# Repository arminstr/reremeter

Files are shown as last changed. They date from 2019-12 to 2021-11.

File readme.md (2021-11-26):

# reremeter

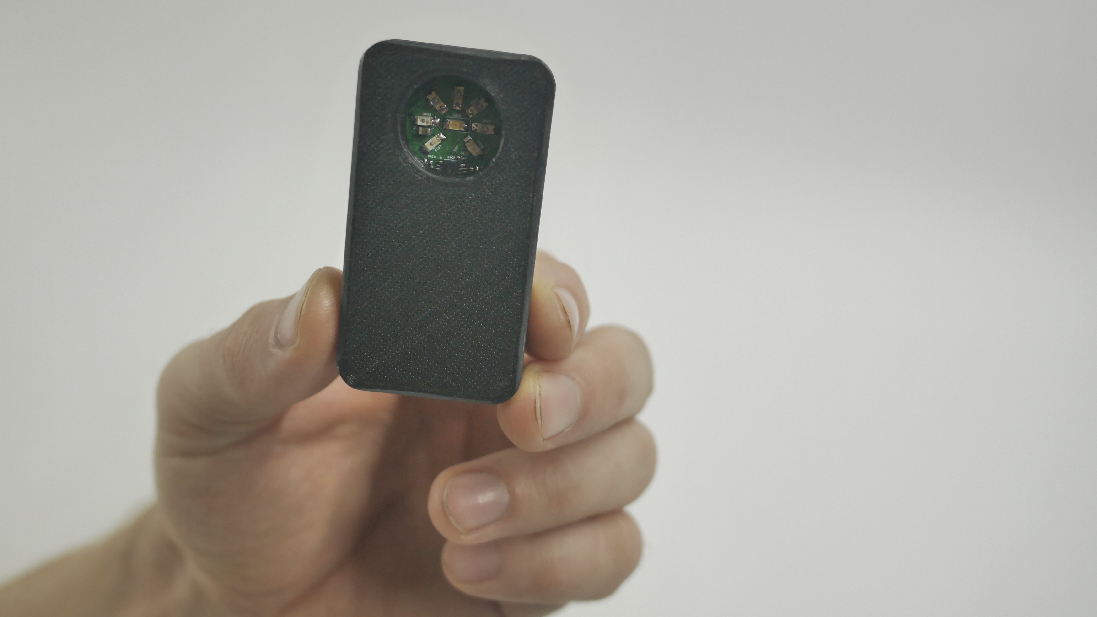
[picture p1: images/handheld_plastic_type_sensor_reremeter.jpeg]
Picture of reremeter


Reremeter is an handheld and low-cost discrete near infrared reflectance spectrometer and a machine learning algorithm developed to detect different types of plastic. Watch our [video](https://www.youtube.com/watch?v=hrVgNUm2_Jo) to find out more!

This repository contains all the files required to build an reremeter from scratch, and you can use them to make your own version. Please take note that this work is published under GPL-3.0. 

### How to get started
> Please note the current *Issues* before getting started with the build of your own reremeter.

Now the guide on how to get started with the build of your own reremeter.
- Build your own [hardware](./hardware).
- Build and upload the [firmware](./firmware).
- Collect data of your samples (or check out our example [dataset](./data)).
- Make Predictions using our provided Python [scripts](./software).
- Visualize results in an [UI](./webapp).

### Additional information 
- The main idea behind this project came from reading this paper about [Identification and classification of plastic resins using near infrared reflectance spectroscopy](https://www.researchgate.net/publication/285330830_Identification_and_classification_of_plastic_resins_using_near_infrared_reflectance_spectroscopy) by Hamed Masoumi, Seyed Mohsen Safavi, and Zahra Khani.
- Inspiration for the analog frontend design was given by the [ADS1255](https://www.ti.com/product/ADS1255) reference designs on the TI website. They used this ADC in several DLP NIR spectrometer designs. (e.g. [DLP® NIRscan™ Evaluation Module](https://www.ti.com/tool/DLPNIRSCANEVM#2), [DLP Ultra-mobile NIR Spectrometer for Portable Chemical Analysis with Bluetooth Connectivity](https://www.ti.com/tool/TIDA-00554))
- Super interesting [MEMS spectrum sensor](https://www.hamamatsu.com/eu/en/product/type/C13272-02/index.html). You can read more about this on [OpenRecycling](https://openrecycling.com/en/projects/2021/01/06/plastic-type-sensor.html). 

### Notes
The reremeter project was created at RealRecycling by Armin Straller and Bernhard Gessler.

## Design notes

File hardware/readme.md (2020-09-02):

# reremeter hardware

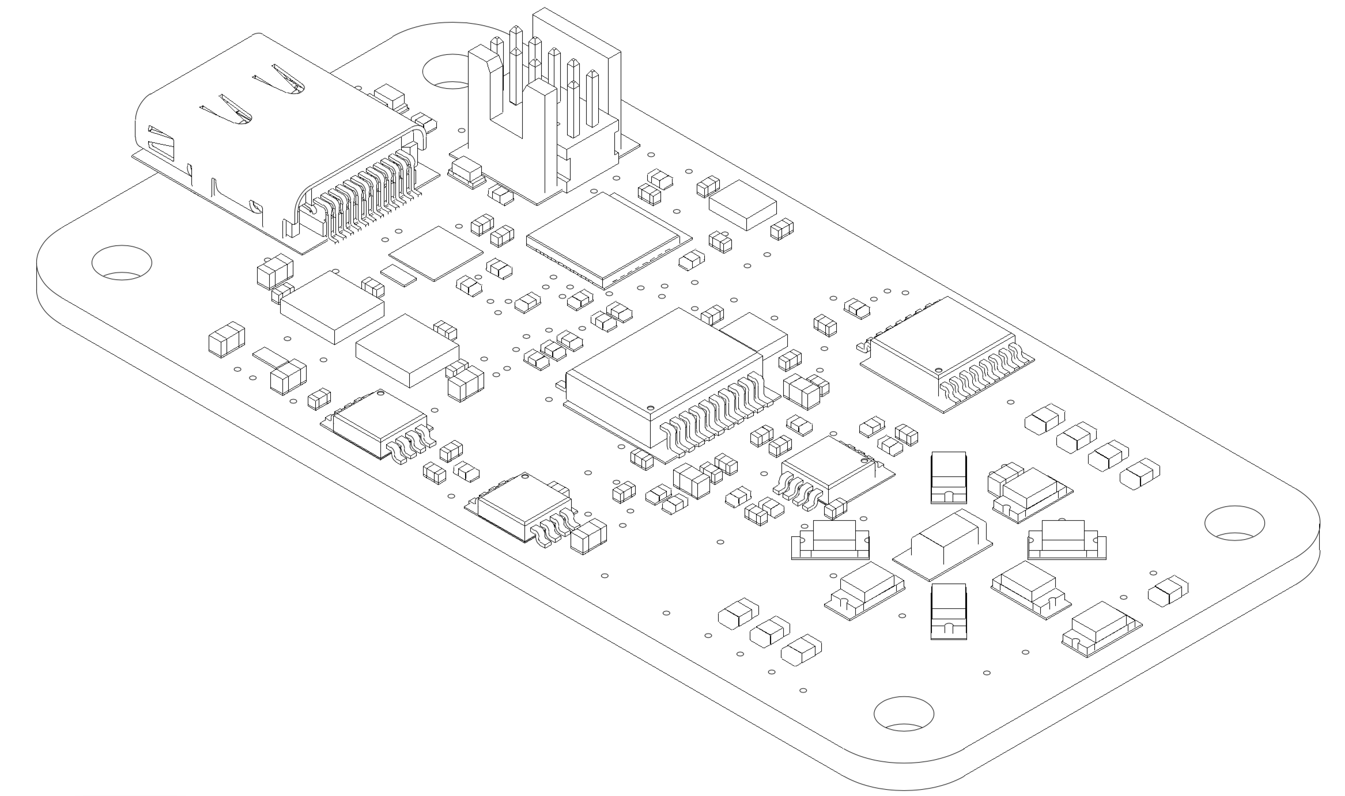
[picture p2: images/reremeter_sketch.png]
Sketch of reremeter exported from CAD model


This folder contains all of the source files for making your own reremeter PCB hardware: a Autodesk Eagle project file for the PCB in spectrometer/, rendered gerber files from the Eagle project in manufacturing/, and exported schematics in this [file](Spectrometer_Schematic.pdf).

The PCB design includes mainly SMT components as the handheld form factor was design criteria. It is possible to assemble individual boards by hand in a few hours (if you bring in decent SMT soldering skills), however for multiple boards it would be advisable to order multiple fully assembled (or at least SMT assembled) PCBs. If you wish to have the PCB manufactured, the files in manufacturing/ should be all you need; additionally, a bill of materials is available [here](manufacturing/Spectrometer_BOM.txt).

Following parts on the BOM previously raised issues:
- X301 is a quartz crystal with 8MHz: FL0800008QDICT-ND
- X302 is a 9pin ARM debug connector: SAM9438-ND
- D20 is a 800nm ~ 1700nm photodetector: 209-003-151-001CT-ND

The mentioned part numbers are from DigiKey. The 8MHz quartz is a replacement part that should fit properly.

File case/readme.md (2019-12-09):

# 3D Printed Case

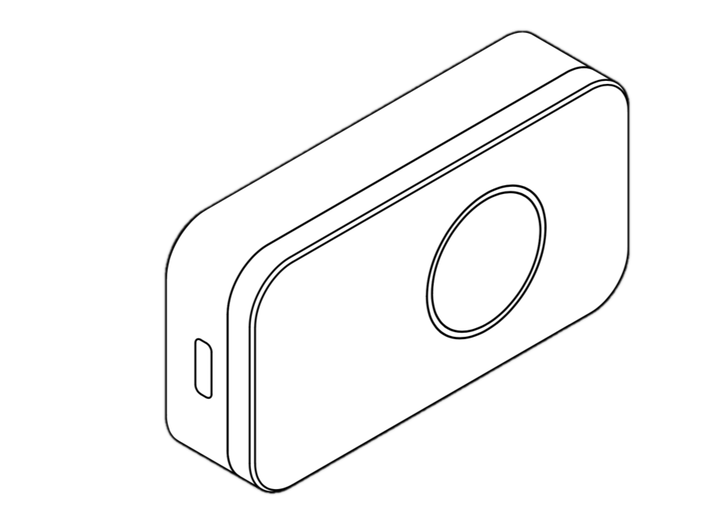
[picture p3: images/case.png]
Picture of case


This directory contains the files we used to 3D print the case for our spectrometer. We highly recommend you printing the same case. It will ensure constant distances to the brightness sensor as well as good handling and protection of the reremeter itself.

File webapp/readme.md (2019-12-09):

# reremeter web interface

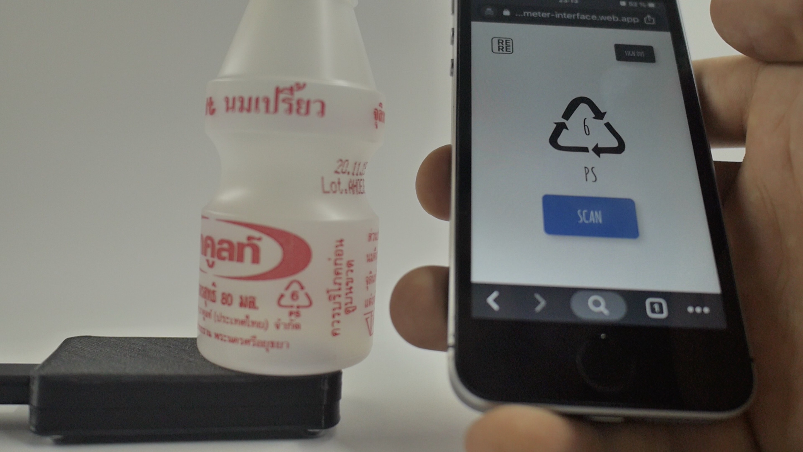
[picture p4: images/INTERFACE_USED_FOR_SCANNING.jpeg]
Picture of web interface


This directory contains the code we used for the scanning interface visible in the above picture. It is a simple HTML, JS and CSS webapp. Using Firebase Authentication and Firebase Realtime Database it is able to run independent of the spectrometers connection. We recommend hosting it with Firebase Hosting for testing.

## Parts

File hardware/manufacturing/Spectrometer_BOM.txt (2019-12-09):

Partlist exported from /Users/armin/CloudStation/02_projects/18_realrecycling/02_dev/01_sensor/02_hardware/pcb/spectrometer/Spectrometer.sch at 07.12.19 15:55

Qty Value                 Device                      Package                 Parts                                                      Description                                 MF MPN               OC_FARNELL OC_NEWARK SPICEPREFIX VALUE    WE-NUMBER               
4   100                   R-EU_R0402                  R0402                   R212, R213, R214, R215                                     RESISTOR, European symbol                                                             R                                            
6   100k                  R-EU_R0402                  R0402                   R108, R208, R209, R210, R211, R308                         RESISTOR, European symbol                                                             R                                            
10  100nF                 C-EUC0402K                  C0402K                  C112, C204, C212, C214, C219, C221, C222, C303, C304, C305 CAPACITOR, European symbol                                                            C                                            
2   100pF                 C-EUC0402K                  C0402K                  C203, C216                                                 CAPACITOR, European symbol                                                            C                                            
2   10k                   R-EU_R0402                  R0402                   R203, R301                                                 RESISTOR, European symbol                                                             R                                            
2   10nF                  C-EUC0402K                  C0402K                  C501, C503                                                 CAPACITOR, European symbol                                                            C                                            
2   10pF                  C-EUC0402K                  C0402K                  C301, C302                                                 CAPACITOR, European symbol                                                            C                                            
2   10uF                  C-EUC0603K                  C0603K                  C504, C513                                                 CAPACITOR, European symbol                                                            C                                            
1   10uF                  C-EUC0805                   C0805                   C201                                                       CAPACITOR, European symbol                                                            C                                            
1   1200nm                LEDCHIPLED_1206             CHIPLED_1206            D105                                                       LED                                                                                                                                
1   1300nm                LEDCHIPLED_1206             CHIPLED_1206            D104                                                       LED                                                                                                                                
1   1450nm                LEDCHIPLED_1206             CHIPLED_1206            D103                                                       LED                                                                                                                                
1   1550nm                LEDCHIPLED_1206             CHIPLED_1206            D102                                                       LED                                                                                                                                
2   15uF                  C-EUC0603K                  C0603K                  C210, C211                                                 CAPACITOR, European symbol                                                            C                                            
1   1650nm                LEDCHIPLED_1206             CHIPLED_1206            D101                                                       LED                                                                                                                                
3   1k                    R-EU_R0402                  R0402                   R302, R303, R304                                           RESISTOR, European symbol                                                             R                                            
1   1k5                   R-EU_R0402                  R0402                   R305                                                       RESISTOR, European symbol                                                             R                                            
6   1uF                   C-EUC0402K                  C0402K                  C207, C208, C209, C307, C502, C507                         CAPACITOR, European symbol                                                            C                                            
2   22R                   R-EU_R0402                  R0402                   R401, R403                                                 RESISTOR, European symbol                                                             R                                            
3   22uF                  C-EUC0805                   C0805                   C105, C205, C206                                           CAPACITOR, European symbol                                                            C                                            
2   240                   WE-CBF_0603_742792631_WB_HS WE-CBF_0603(W=2.2)      FB201, FB401                                               WE-CBF SMD EMI Suppression Ferrite Bead                                                                    742792631/240Ω(Z@100MHz)
2   240k                  R-EU_R0402                  R0402                   R206, R207                                                 RESISTOR, European symbol                                                             R                                            
2   301                   R-EU_R0402                  R0402                   R204, R205                                                 RESISTOR, European symbol                                                             R                                            
1   36                    R-EU_R0603                  R0603                   R107                                                       RESISTOR, European symbol                                                             R                                            
1   39                    R-EU_R0603                  R0603                   R106                                                       RESISTOR, European symbol                                                             R                                            
5   43                    R-EU_R0603                  R0603                   R101, R102, R103, R104, R105                               RESISTOR, European symbol                                                             R                                            
1   47nF                  C-EUC0402K                  C0402K                  C215                                                       CAPACITOR, European symbol                                                            C                                            
2   49.9                  R-EU_R0402                  R0402                   R201, R202                                                 RESISTOR, European symbol                                                             R                                            
2   51pF                  C-EUC0402K                  C0402K                  C217, C218                                                 CAPACITOR, European symbol                                                            C                                            
1   5Vdc/2pF              WE-TVS_SOT23-6L_82400102    WE-TVS_SOT23-6L         D401                                                       WE-TVS TVS Diode – High Speed Series                                                              5Vdc/2pF 82400102                
2   5k1                   R-EU_R0402                  R0402                   R402, R404                                                 RESISTOR, European symbol                                                             R                                            
1   6.8                   R-EU_R0603                  R0603                   R109                                                       RESISTOR, European symbol                                                             R                                            
1   632723300011THT       632723300011THT             USBC_HORZONTAL_WE       X401                                                                                                                                                                                          
1   850nm                 LEDCHIPLED_1206             CHIPLED_1206            D107                                                       LED                                                                                                                                
1   8MHz                  CRYSTALS-GND-LID-CFPX-218   2.6X2.1-4-PAD           X301                                                       CRYSTALS WITH CAN GROUNDED                                                                                                         
1   940nm                 LEDCHIPLED_1206             CHIPLED_1206            D106                                                       LED                                                                                                                                
1   ADS1255TSSOP          ADS1255TSSOP                SOP65P780X200-20        U201                                                                                                                                                                                          
1   CORTEX-MDEBUG-10P     CORTEX-MDEBUG-10P           CORTEX-M-CON-10P        X302                                                                                                                                                                                          
1   LT1763IDE-3.3         LT1763IDE-3.3               DFN12                   IC501                                                      500mA, Low Noise, LDO Micropower Regulators    LT1763IDE-3.3#PBF 1783320    51R1529                                                
1   LT1763IDE-5           LT1763IDE-5                 DFN12                   IC502                                                      500mA, Low Noise, LDO Micropower Regulators    LT1763IDE-5#PBF   1839222    51R1531                                                
4   MOUNT-HOLE2.8         MOUNT-HOLE2.8               2,8                     H1, H2, H3, H4                                             MOUNTING HOLE with drill center marker                                                                                             
1   OPA2376PDSO-8         OPA2376PDSO-8               SOP65P490X110-8         U202                                                                                                                                                                                          
1   OPA350PDSO-8          OPA350PDSO-8                SOP65P490X110-8         U203                                                                                                                                                                                          
1   REF5025PDSO-8         REF5025PDSO-8               SOP65P490X110-8         U204                                                                                                                                                                                          
1   SD003-151-001SMD      SD003-151-001SMD            LEDC3316X110            D201                                                       Surface-Mount InGaAs Photodetector                                                                                                 
1   STM32F302K8U6UFQFPN32 STM32F302K8U6UFQFPN32       QFN50P500X500X60-33T350 U301                                                                                                                                                                                          
1   TLC59208FTSSOP-16     TLC59208FTSSOP-16           SOP65P640X120-16        U101                                                       TLC59208F 8-Bit Fm+ I2C Bus LED Driver                                                                                             
2   green                 LEDCHIP-LED0603             CHIP-LED0603            D301, D303                                                 LED                                                                                                                                
1   orange                LEDCHIP-LED0603             CHIP-LED0603            D302                                                       LED                                                                                                                                
1   white                 LEDCHIPLED_1206             CHIPLED_1206            D108                                                       LED

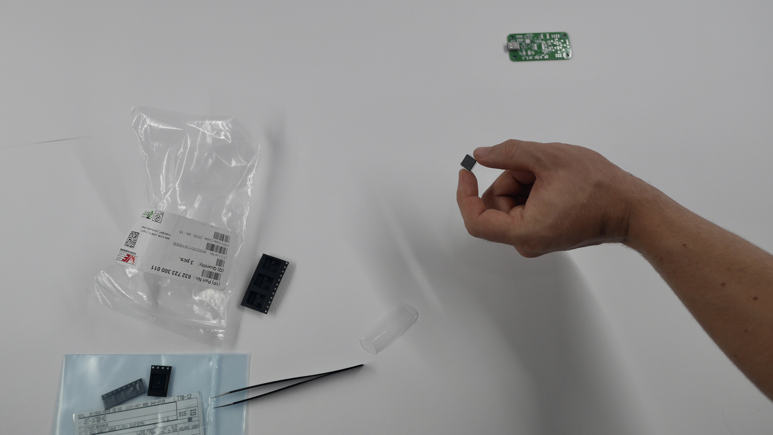
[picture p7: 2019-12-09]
images/PARTS_AND_ASSEMBLY.jpeg

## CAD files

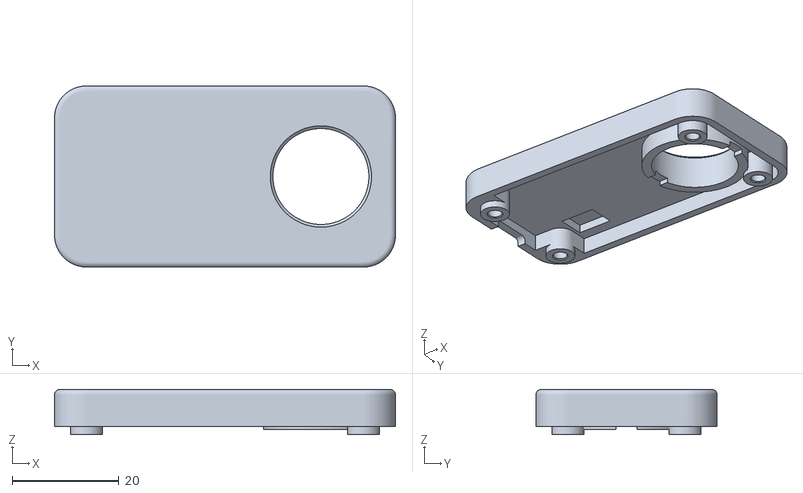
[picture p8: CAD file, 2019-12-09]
case/Spectrometer_Case_Part1.stl
64.0 x 34.0 x 8.50

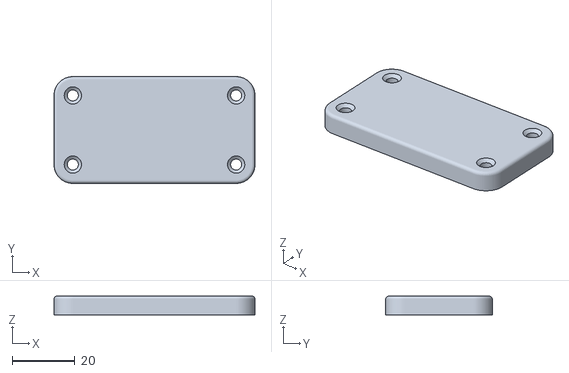
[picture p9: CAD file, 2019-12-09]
case/Spectrometer_Case_Part2.stl
64.0 x 34.0 x 6.00

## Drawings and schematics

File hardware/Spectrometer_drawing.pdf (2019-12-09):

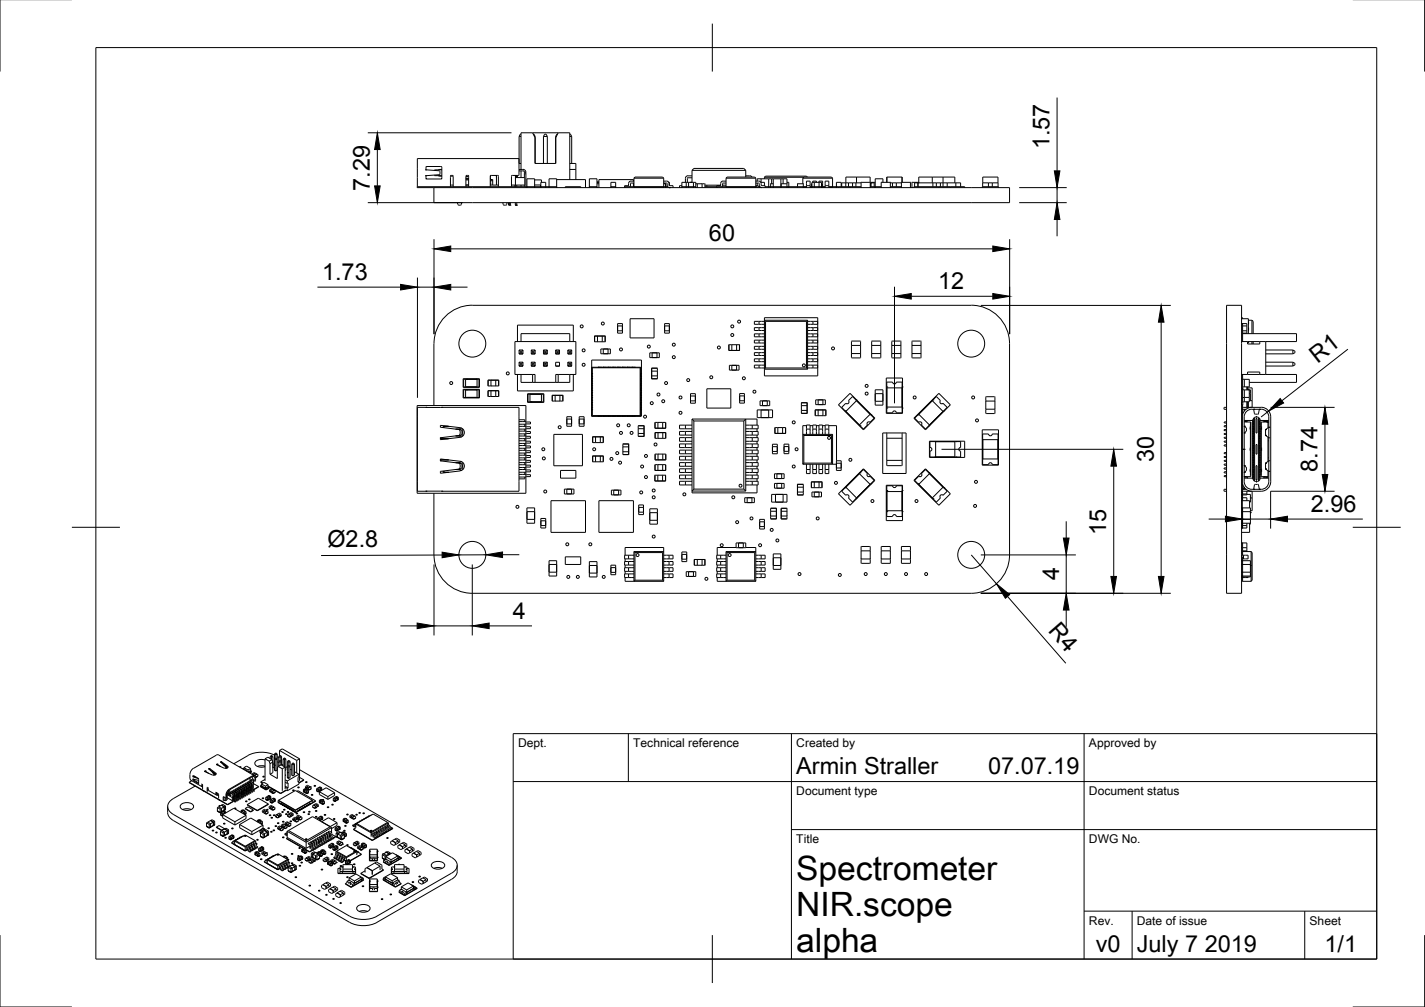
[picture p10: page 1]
Dept.; Technical reference; Created by; Approved by; Document type; Document status; Title; DWG No.; Rev.; Date of issue; Sheet; alpha; v0 July 7 2019; Armin Straller

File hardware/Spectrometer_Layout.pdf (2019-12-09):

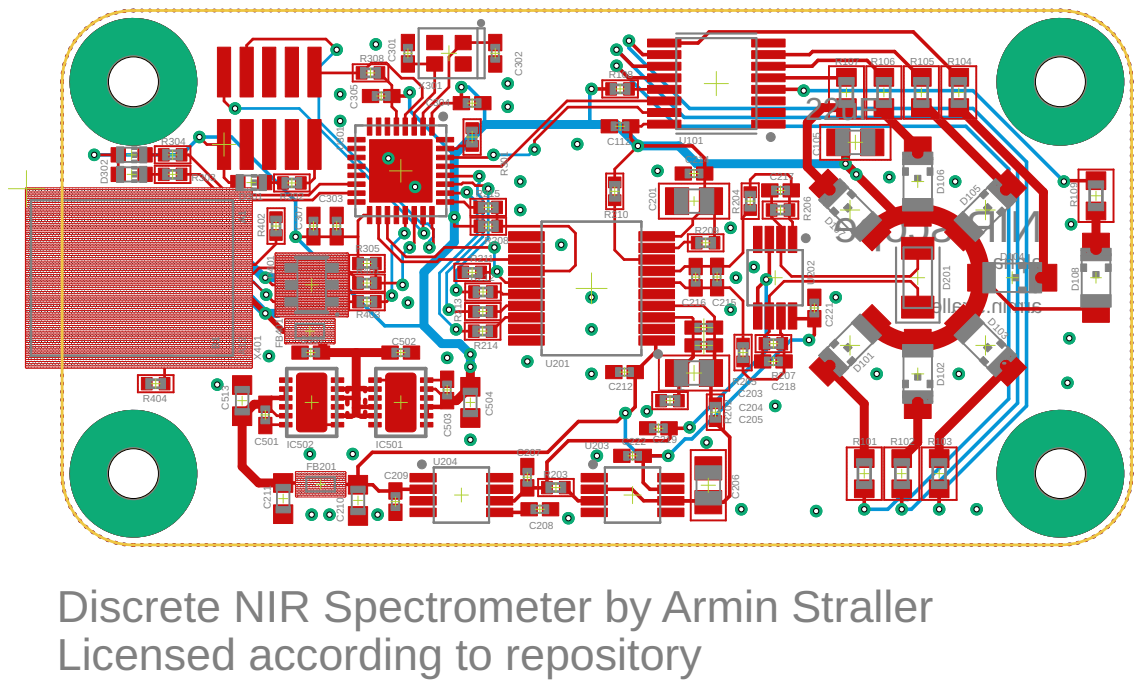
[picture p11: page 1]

Discrete NIR Spectrometer by Armin Straller
Licensed according to repository

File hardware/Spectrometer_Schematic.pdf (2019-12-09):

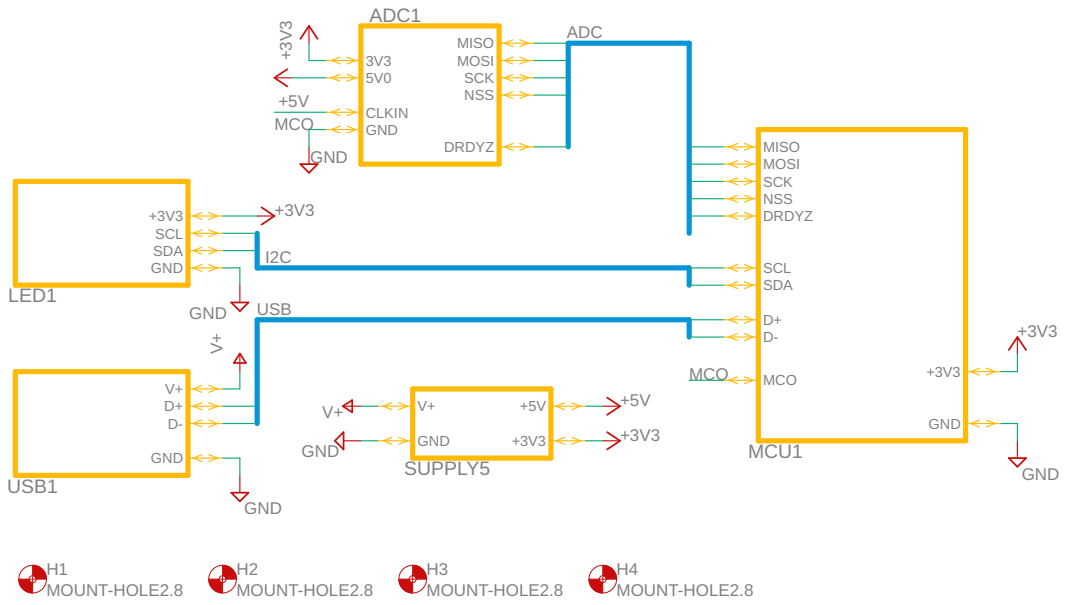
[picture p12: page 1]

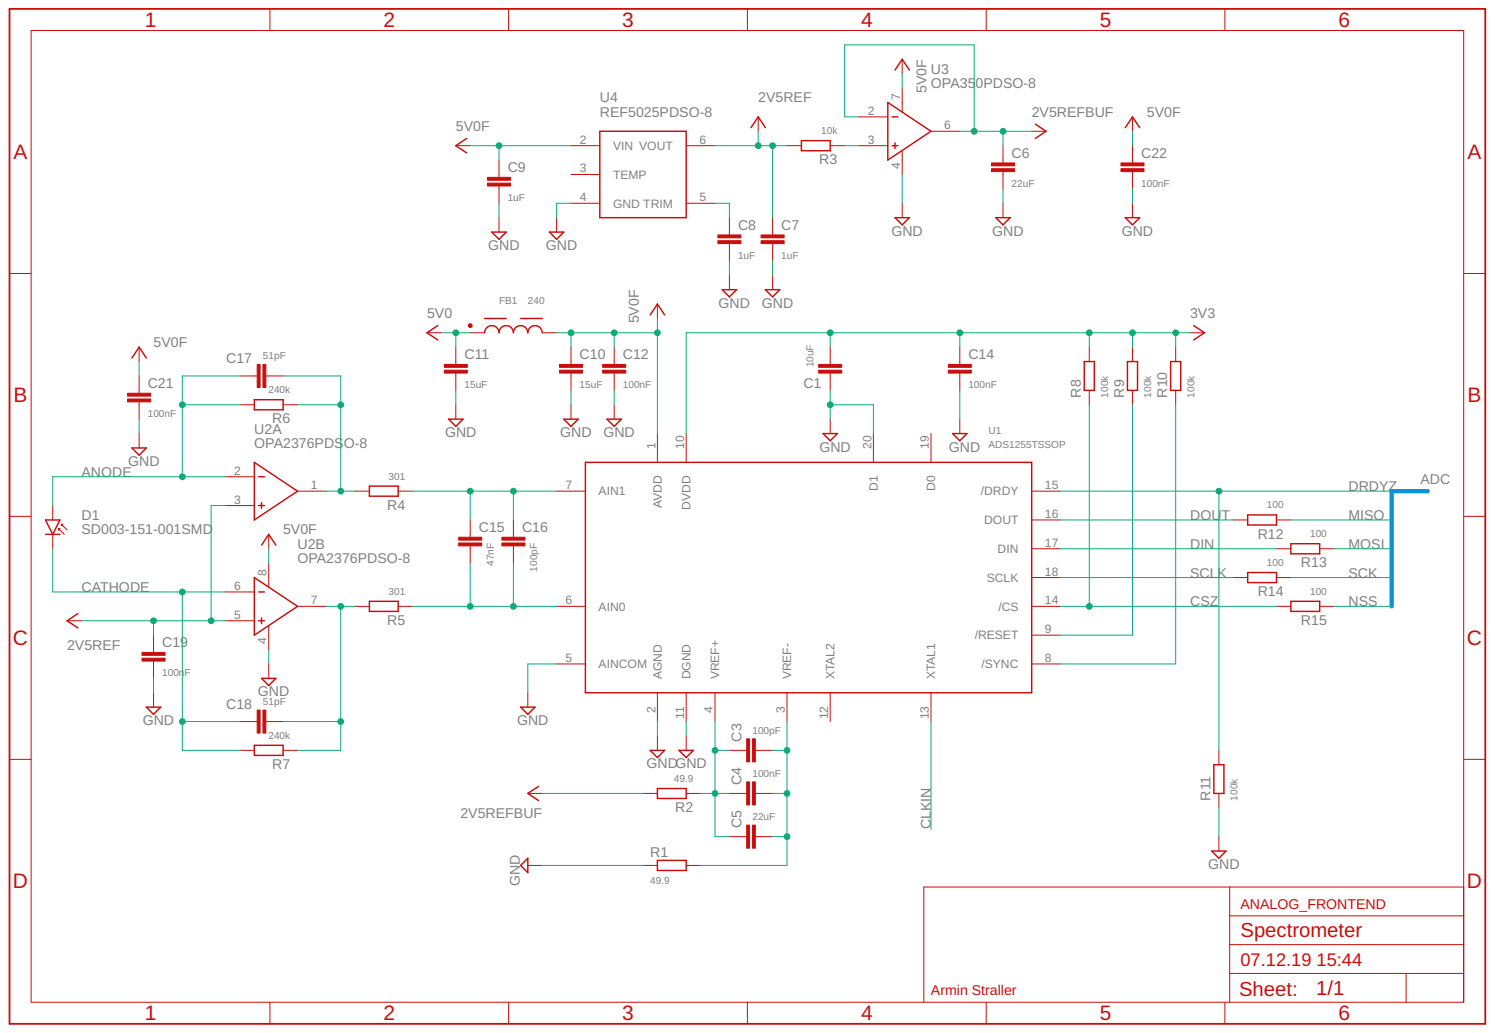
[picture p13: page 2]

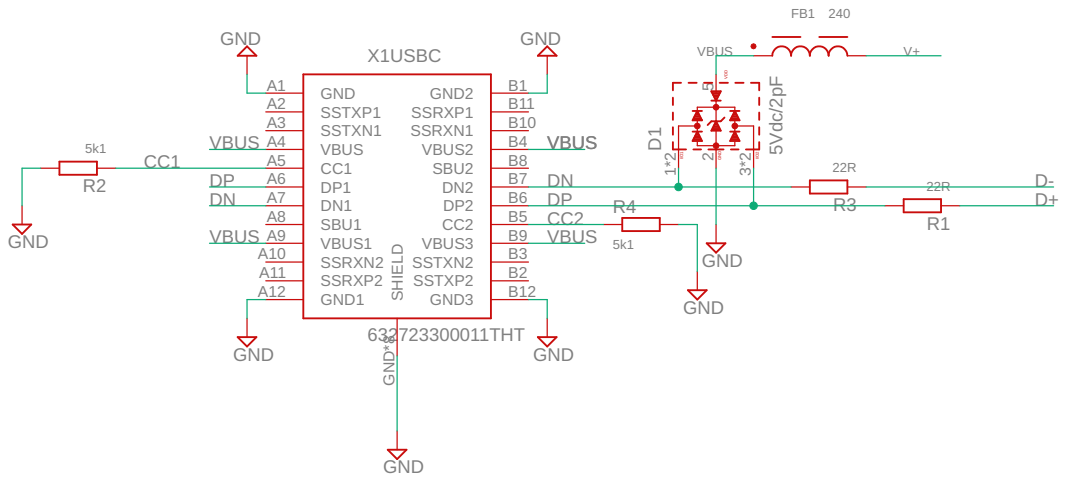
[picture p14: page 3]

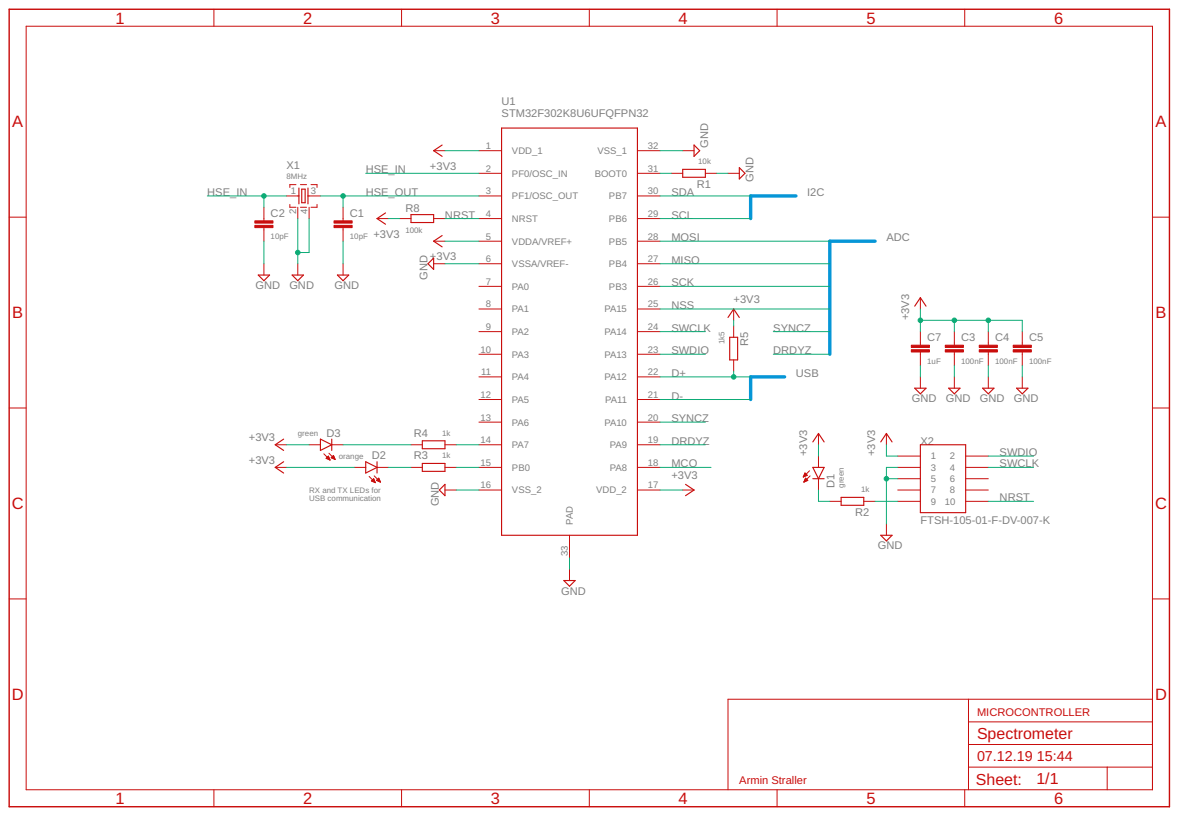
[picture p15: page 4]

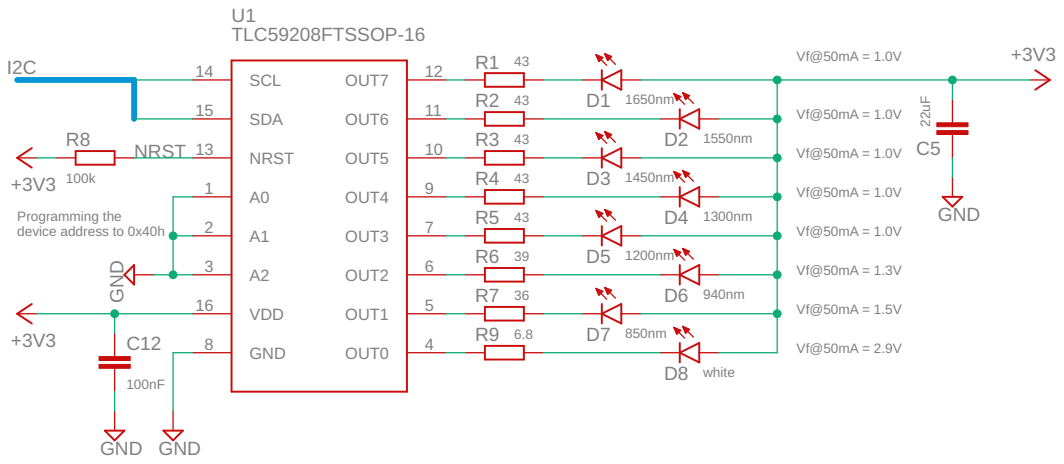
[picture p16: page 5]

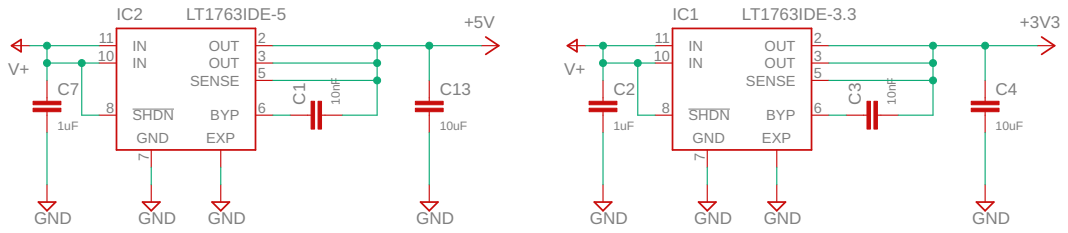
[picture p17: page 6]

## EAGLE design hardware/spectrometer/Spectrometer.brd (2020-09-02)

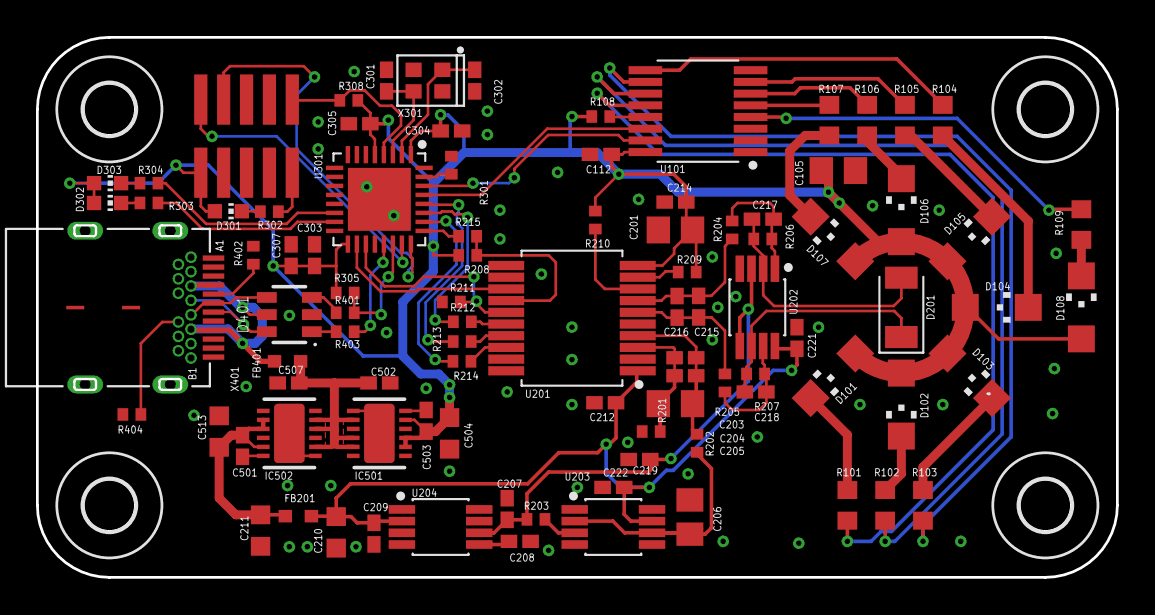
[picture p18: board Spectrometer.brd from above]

Board: 2 copper layers, 60.0 x 30.0 mm, 97 parts (0 on the bottom side), 69 nets.

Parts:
C105, C205, C206: 22uF; C0805
C112, C204, C212, C214, C219, C221, C222, C303, C304, C305: 100nF; C0402K
C201: 10uF; C0805
C203, C216: 100pF; C0402K
C207, C208, C209, C307, C502, C507: 1uF; C0402K
C210, C211: 15uF; C0603K
C215: 47nF; C0402K
C217, C218: 51pF; C0402K
C301, C302: 10pF; C0402K
C501, C503: 10nF; C0402K
C504, C513: 10uF; C0603K
D101: 1650nm; CHIPLED_1206
D102: 1550nm; CHIPLED_1206
D103: 1450nm; CHIPLED_1206
D104: 1300nm; CHIPLED_1206
D105: 1200nm; CHIPLED_1206
D106: 940nm; CHIPLED_1206
D107: 850nm; CHIPLED_1206
D108: white; CHIPLED_1206
D201: SD003-151-001SMD; LEDC3316X110
D301, D303: green; CHIP-LED0603
D302: orange; CHIP-LED0603
D401: 5Vdc; WE-TVS_SOT23-6L
FB201, FB401: 240Ohm@100MHz; WE-CBF_0603(W=2.2)
H1, H2, H3, H4: MOUNT-HOLE2.8; 2,8
IC501: LT1763IDE-3.3; DFN12
IC502: LT1763IDE-5; DFN12
R101, R102, R103, R104, R105: 43; R0603
R106: 39; R0603
R107: 36; R0603
R108, R208, R209, R210, R211, R308: 100k; R0402
R109: 6.8; R0603
R201, R202: 49.9; R0402
R203, R301: 10k; R0402
R204, R205: 301; R0402
R206, R207: 240k; R0402
R212, R213, R214, R215: 100; R0402
R302, R303, R304: 1k; R0402
R305: 1k5; R0402
R401, R403: 22R; R0402
R402, R404: 5k1; R0402
U101: TLC59208FTSSOP-16; SOP65P640X120-16
U201: ADS1255TSSOP; SOP65P780X200-20
U202: OPA2376PDSO-8; SOP65P490X110-8
U203: OPA350PDSO-8; SOP65P490X110-8
U204: REF5025PDSO-8; SOP65P490X110-8
U301: STM32F302K8U6UFQFPN32; QFN50P500X500X60-33T350
X301: 8MHz; 2.6X2.1-4-PAD
X302: CORTEX-MDEBUG-10P; CORTEX-M-CON-10P
X401: 632723300011THT; USBC_HORZONTAL_WE

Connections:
+3V3: C105.2, C112.1, C201.2, C214.1, C303.1, C304.1, C305.1, C307.1, C503.2, C504.2, D101.A, D102.A, D103.A, D104.A, D105.A, D106.A, D107.A, D108.A, D301.A, D302.A, D303.A, IC501.2, IC501.3, IC501.5, R108.1, R208.2, R209.2, R210.2, R305.1, R308.1, U101.16, U201.10, U301.1, U301.5, U301.17, X302.P$1
+5V: C211.2, C501.2, C513.2, FB201.1, IC502.2, IC502.3, IC502.5
ADC1:2V5REF: C207.1, C219.1, R203.2, U202.3, U202.5, U204.6
ADC1:2V5REFBUF: C206.2, R202.2, U203.2, U203.6
ADC1:5V0F: C209.1, C210.2, C212.1, C221.1, C222.1, FB201.2, U201.1, U202.8, U203.7, U204.2
ADC1:ANODE: C217.1, D201.2, R206.2, U202.2
ADC1:CATHODE: C218.1, D201.1, R207.2, U202.6
ADC1:CSZ: R208.1, R215.2, U201.14
ADC1:DIN: R213.2, U201.17
ADC1:DOUT: R212.2, U201.16
ADC1:N$3: C203.2, C204.2, C205.2, R201.2, U201.3
ADC1:N$4: C203.1, C204.1, C205.1, R202.1, U201.4
ADC1:N$5: R203.1, U203.3
ADC1:N$6: C208.1, U204.5
ADC1:N$7: C217.2, R204.2, R206.1, U202.1
ADC1:N$8: C218.2, R205.2, R207.1, U202.7
ADC1:N$9: C215.2, C216.2, R205.1, U201.6
ADC1:N$10: C215.1, C216.1, R204.1, U201.7
ADC1:N$11: R209.1, U201.9
ADC1:SCLK: R214.2, U201.18
ADC1:SYNCZ: R210.1, U201.8
D+: R305.2, R401.1, U301.22
D-: R403.1, U301.21
DRDYZ: R211.2, U201.15, U301.19
GND: C105.1, C112.2, C201.1, C206.1, C207.2, C208.2, C209.2, C210.1, C211.1, C212.2, C214.2, C219.2, C221.2, C222.2, C301.2, C302.2, C303.2, C304.2, C305.2, C307.2, C502.2, C504.1, C507.2, C513.1, D401.2, IC501.7, IC501.EXP, IC502.7, IC502.EXP, R201.1, R211.1, R301.1, R402.2, R404.2, U101.1, U101.2, U101.3, U101.8, U201.2, U201.5, U201.11, U201.20, U202.4, U203.4, U204.4, U301.6, U301.16, U301.32, U301.33, X301.2, X301.4, X302.P$3, X302.P$5, X401.A1, X401.A12, X401.B1, X401.B12, X401.GND, X401.GND1, X401.Z1, X401.Z2, X401.Z3, X401.Z4, X401.Z5, X401.Z6
LED1:N$1: R101.1, U101.12
LED1:N$2: R102.1, U101.11
LED1:N$3: R103.1, U101.10
LED1:N$4: R104.1, U101.9
LED1:N$5: R105.1, U101.7
LED1:N$6: R106.1, U101.6
LED1:N$7: R107.1, U101.5
LED1:N$8: R109.1, U101.4
LED1:N$9: D108.C, R109.2
LED1:N$10: D107.C, R107.2
LED1:N$11: D106.C, R106.2
LED1:N$12: D105.C, R105.2
LED1:N$13: D104.C, R104.2
LED1:N$14: D103.C, R103.2
LED1:N$15: D102.C, R102.2
LED1:N$16: D101.C, R101.2
LED1:NRST: R108.2, U101.13
MCO: U201.13, U301.18
MCU1:HSE_IN: C302.1, U301.2, X301.1
MCU1:HSE_OUT: C301.1, U301.3, X301.3
MCU1:N$1: R304.1, U301.14
MCU1:N$2: R301.2, U301.31
MCU1:N$3: R302.1, X302.P$9
MCU1:N$4: D301.C, R302.2
MCU1:N$5: R303.1, U301.15
MCU1:N$6: D303.C, R304.2
MCU1:N$7: D302.C, R303.2
MCU1:NRST: R308.2, U301.4, X302.P$10
MCU1:SWCLK: U301.24, X302.P$4
MCU1:SWDIO: U301.23, X302.P$2
MISO: R212.1, U301.27
MOSI: R213.1, U301.28
NSS: R215.1, U301.25
SCK: R214.1, U301.26
SCL: U101.14, U301.29
SDA: U101.15, U301.30
SUPPLY5:N$1: C501.1, IC502.6
SUPPLY5:N$2: C503.1, IC501.6
USB1:CC1: R402.1, X401.A5
USB1:CC2: R404.1, X401.B5
USB1:DN: D401.1, D401.6, R403.2, X401.A7, X401.B7
USB1:DP: D401.3, D401.4, R401.2, X401.A6, X401.B6
USB1:VBUS: D401.5, FB401.1, X401.A4, X401.A9, X401.B4, X401.B9
V+: C502.1, C507.1, FB401.2, IC501.8, IC501.10, IC501.11, IC502.8, IC502.10, IC502.11

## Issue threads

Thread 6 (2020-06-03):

### ISSUE TITLE
Making a simpler add on board

### ISSUE THREAD

**Issue by mattkanwisher** [arminstr/reremeter#6]
I’m curious, what parts would be needed to make this more into an add on board for a raspberry pi or an Arduino? Seems like it would saving a lot of engineering to use an off the shelf board, to integrate into industrial settings. Have you explored this at all?

**Comment by arminstr** [comment]
You could basically replace the STM32F3 by the required board (Arduino / Raspberry Pi). As the ADC and the LED driver are interfaced using SPI/I2C you could simply connect those to the board using pin headers (you might have to add level shifters). 
Some potential issues might be:
- Bad debugging possibilities 
- Slow measurement time 
- More expensive
- The other issues mentioned in this repository

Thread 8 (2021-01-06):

### ISSUE TITLE
Recycling in Germany

### ISSUE THREAD

**Issue by Frinkew** [arminstr/reremeter#8]
Hey,

I m currently starting a recycling project in Germany, Karlsruhe.
We are working in the Offene Jugendwerkstatt Karlsruhe and want to teach pupils and young adults how to recycle plastic.

It would be nice if you could answer some questions about your reremeter personally.

You can contact me via Mail: F.Rinkewitz@gmail.com

P.s. your website is down.

Yours sincerely
Felix

**Comment by arminstr** [comment]
Frinkew and I had a video call back then. 
Currently, I recommend building the [reremeter version](https://github.com/Jerzeek/PlasticScanner) by Jerry.

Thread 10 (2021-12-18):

### ISSUE TITLE
LED Wavelength

### ISSUE THREAD

**Issue by NobleOMD** [arminstr/reremeter#10]
In your [BOM](https://github.com/arminstr/reremeter/blob/master/hardware/manufacturing/Spectrometer_BOM.txt) you are using 1206LEDs. How are you controlling the wavelength for each LED, is it a filter, by sorting (like with resistors) or actually a different LED spec per wavelength?

**Comment by arminstr** [comment]
The system uses discrete Near-Infrared LEDs. Therefore you will need LEDs with different wavelength specifications. We previously sourced them via DigiKey. The manufacturer is Marktech Optoelectronics.

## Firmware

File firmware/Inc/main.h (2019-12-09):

/* USER CODE BEGIN Header */
/**
  ******************************************************************************
  * @file           : main.h
  * @brief          : Header for main.c file.
  *                   This file contains the common defines of the application.
  ******************************************************************************
  * @attention
  *
  * <h2><center>&copy; Copyright (c) 2019 STMicroelectronics.
  * All rights reserved.</center></h2>
  *
  * This software component is licensed by ST under Ultimate Liberty license
  * SLA0044, the "License"; You may not use this file except in compliance with
  * the License. You may obtain a copy of the License at:
  *                             www.st.com/SLA0044
  *
  ******************************************************************************
  */
/* USER CODE END Header */

/* Define to prevent recursive inclusion -------------------------------------*/
#ifndef __MAIN_H
#define __MAIN_H

#ifdef __cplusplus
extern "C" {
#endif

/* Includes ------------------------------------------------------------------*/
#include "stm32f3xx_hal.h"

/* Private includes ----------------------------------------------------------*/
/* USER CODE BEGIN Includes */

/* USER CODE END Includes */

/* Exported types ------------------------------------------------------------*/
/* USER CODE BEGIN ET */

/* USER CODE END ET */

/* Exported constants --------------------------------------------------------*/
/* USER CODE BEGIN EC */

/* USER CODE END EC */

/* Exported macro ------------------------------------------------------------*/
/* USER CODE BEGIN EM */

/* USER CODE END EM */

/* Exported functions prototypes ---------------------------------------------*/
void Error_Handler(void);

/* USER CODE BEGIN EFP */

/* USER CODE END EFP */

/* Private defines -----------------------------------------------------------*/
#define greenLED_Pin GPIO_PIN_7
#define greenLED_GPIO_Port GPIOA
#define orangeLED_Pin GPIO_PIN_0
#define orangeLED_GPIO_Port GPIOB
#define NDRDY_Pin GPIO_PIN_9
#define NDRDY_GPIO_Port GPIOA
#define NSYNC_Pin GPIO_PIN_10
#define NSYNC_GPIO_Port GPIOA
#define SPI3_NSS_Pin GPIO_PIN_15
#define SPI3_NSS_GPIO_Port GPIOA
/* USER CODE BEGIN Private defines */

/* USER CODE END Private defines */

#ifdef __cplusplus
}
#endif

#endif /* __MAIN_H */

/************************ (C) COPYRIGHT STMicroelectronics *****END OF FILE****/

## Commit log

2019-12-09 Edited case and webapp readme.md
2020-09-02 changed library dependencies
    [Spectrometer.brd, Spectrometer.sch]

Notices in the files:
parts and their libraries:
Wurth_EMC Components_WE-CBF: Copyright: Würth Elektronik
